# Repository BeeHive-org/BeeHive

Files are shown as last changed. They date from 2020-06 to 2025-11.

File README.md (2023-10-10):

# BeeHive - a flexible platform for connecting different sensors and actuators

## Intro

This project started as a collaboration between [Ihor Sobianin](https://github.com/isobianin/) and [Andre Chagas](https://github.com/amchagas/), after some chats about improving the [FlyPi design](https://github.com/amchagas/flypi). 

## Hardware 

The idea here is to make a very flexible hardware system that is easy to expand/customize for lab applications. The very initial implementation consists of:
- a hub PCB - which contains:
   -  2 voltage regulators that step down voltage from 12V to 5V and supply these 3 voltages to specific pins throughout the board.
   -  a central slot for an [ESP32 WROOM](https://www.espressif.com/sites/default/files/documentation/esp32-wroom-32_datasheet_en.pdf) and the breakout of all its pins into JST connectors.
   - Two Mikroe MikroBus connectors (https://www.mikroe.com/mikrobus).
   - Two Sparkfun Qwiic connectore (https://www.sparkfun.com/qwiic).
   - A 3.3V onboard voltage regulator.

-  4 switch array with an [TPIC6B595 shift register](https://www.ti.com/lit/ds/symlink/tpic6b595.pdf) and transistors.

-  8 switch array with an [TPIC6B595 shift register](https://www.ti.com/lit/ds/symlink/tpic6b595.pdf) and transistors.

-  12V5A breakout which is based on simple barrel jack connector and JST connectors

-  power supply which are based on the [LM2596 T5](https://www.ti.com/lit/ds/symlink/lm2596.pdf) a step down switching regulator
For more details see [current design](#the-current-design) section below.  

## Software

On the software side of things we are initially running micropython, as this will offer a low entry barrier for researchers (as Python is more and more the chosen language for much of the scientific stack).

- The current implementation runs stock micropython with [OSC library](https://github.com/SpotlightKid/micropython-osc) for communication, as this will allow easy integration with [Bonsai-RX](https://bonsai-rx.org/), a powerful piece of software that has integrations with other interesting open source tools for science, such as [open ephys](https://open-ephys.org/), [DeepLab Cut](http://www.mousemotorlab.org/deeplabcut) and other proprietary but useful tools, like high speed cameras, National Instruments DAQ systems. 

- The main wish software wise for this project is to make it compatible with [Labthings](https://github.com/labthings).

---

## The current design

### The main hub:

#### Schematics

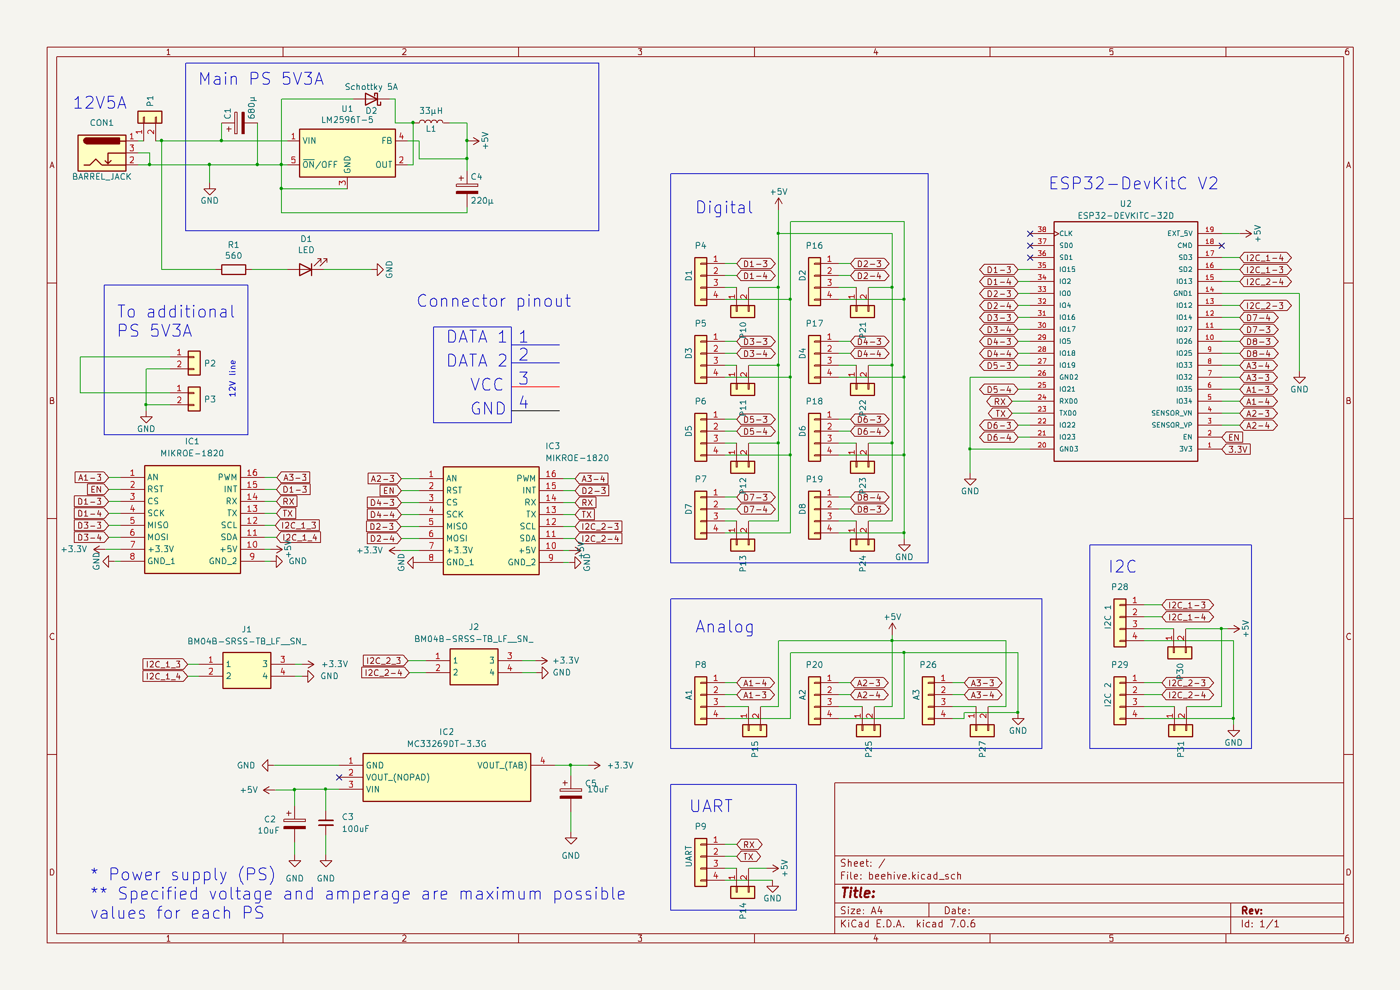
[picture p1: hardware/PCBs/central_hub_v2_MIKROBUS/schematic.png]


#### PCB

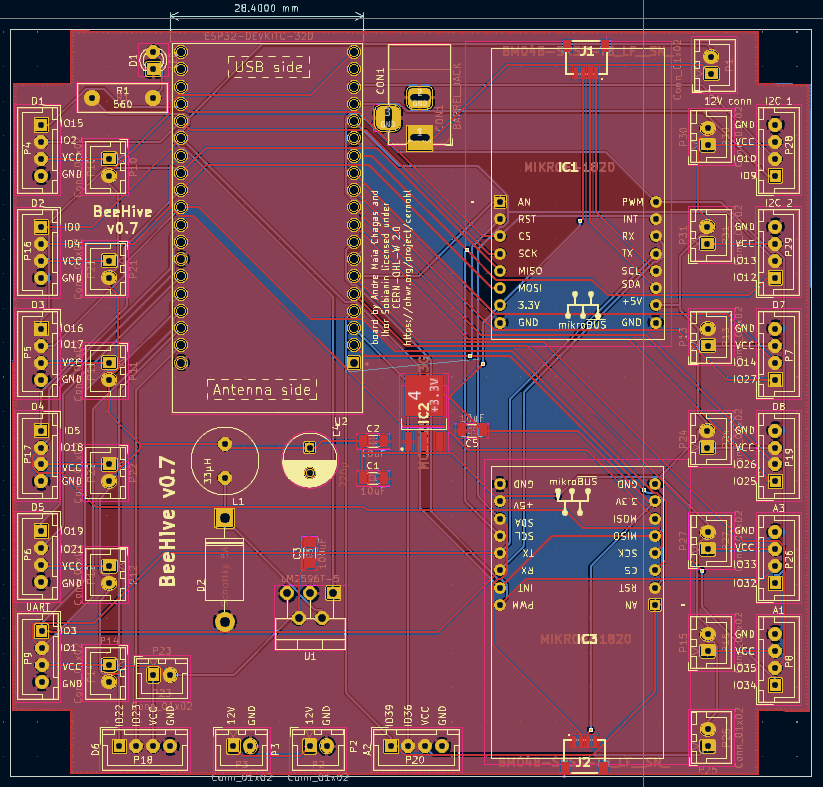
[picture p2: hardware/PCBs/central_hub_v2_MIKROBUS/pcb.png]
beehive_PCB


### The power supply module:

#### Schematics

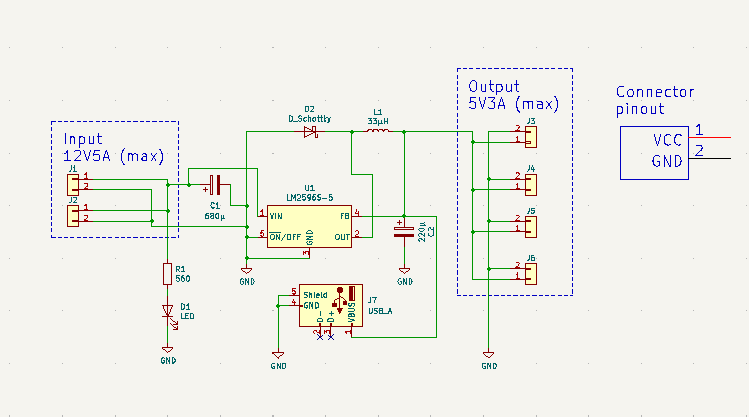
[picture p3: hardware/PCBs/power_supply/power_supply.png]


#### PCB

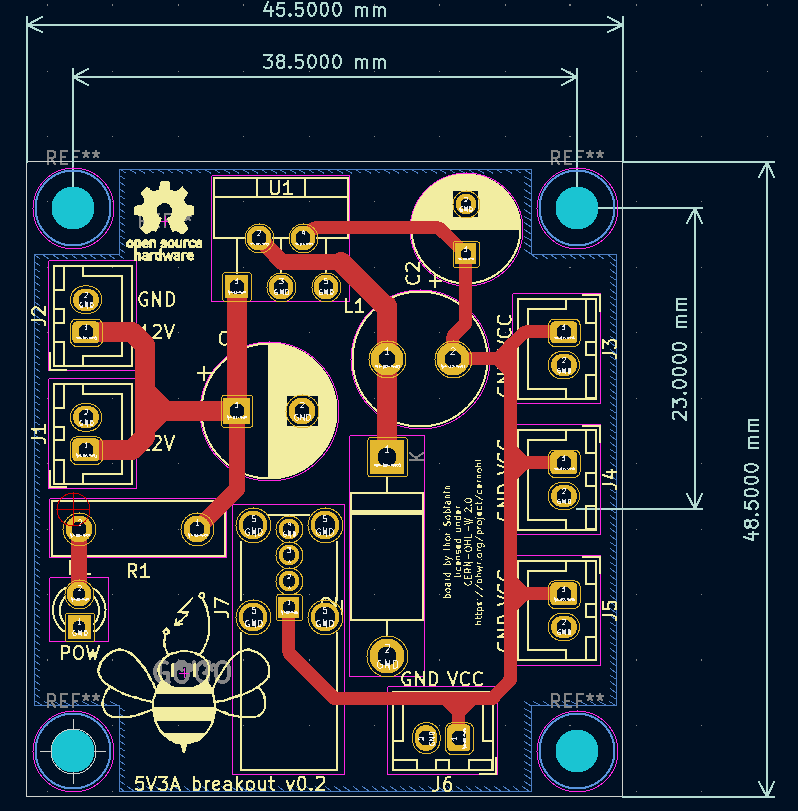
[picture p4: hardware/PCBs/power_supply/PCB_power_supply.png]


### The transistor-switch hub for 8 devices:

#### Schematics

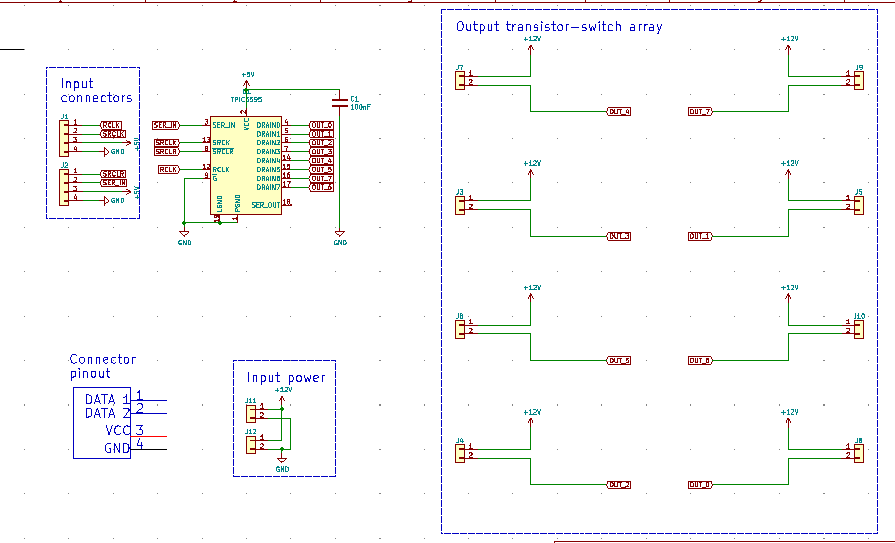
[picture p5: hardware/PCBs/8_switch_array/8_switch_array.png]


#### PCB

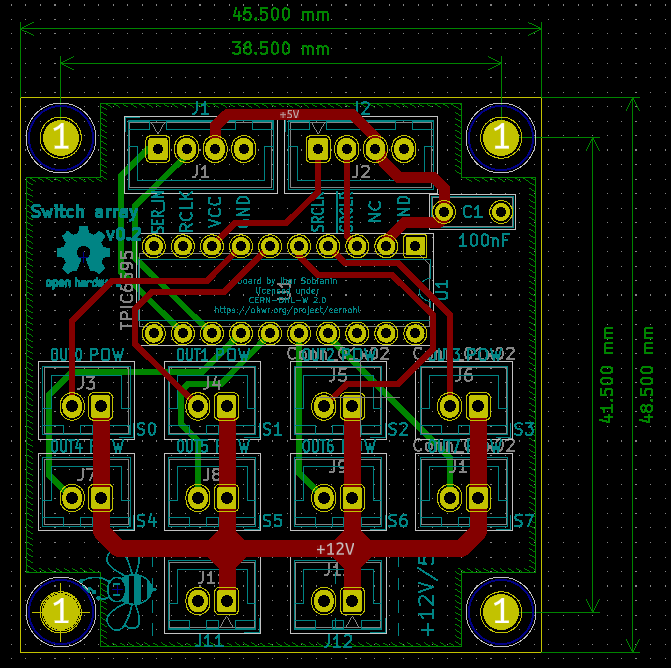
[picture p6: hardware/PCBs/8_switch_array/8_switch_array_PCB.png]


---

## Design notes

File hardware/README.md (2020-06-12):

In this folder users & collaborators will find designs and considerations about the hardware parts being developed in this project. 

### hub_PCB:
- the central part of the system, is mainly a breakout board for the ESP32 being used and two built in power supplies. 

The pin mapping of the ESP32 controller and our board can be seen here:

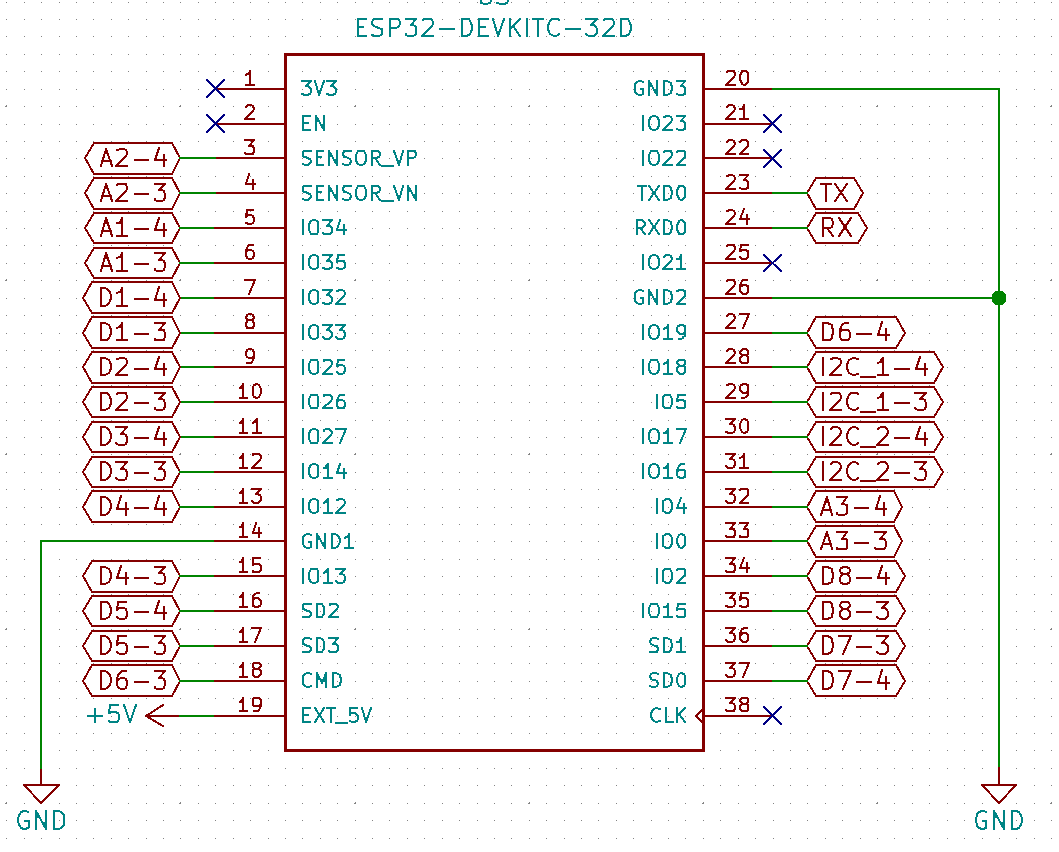
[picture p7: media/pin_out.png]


Using table 2 of this [manual](https://www.espressif.com/sites/default/files/documentation/esp32-wroom-32_datasheet_en.pdf) we can see all the options for each pin.

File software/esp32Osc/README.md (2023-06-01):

# Bonsai + BeeHive

The scripts in this folder are a first test for integration [Bonsai-RX](bonsai-rx.org) with BeeHive using [OSC](http://opensoundcontrol.org) protocol.

The idea is pretty simple for the moment:

Digital:
- make half of the Digital pins as inputs (DI)
- make half of the Digital pins as outputs (DO)
- set the ESP32 to scan the state of all DI pins and send that information out as one integer in an OSC message
- set the ESP32 to listen to OSC messages with one integer and decode that to set DO pins

Analog:
- Read all analog pin states and send that information out as an OSC message
- Set the ESP32 to listen to OSC messages (one integer to determine analog output port and another integer to determine value to be written) and write analog output value

| <Function Call> | <Return Function> | <Event> |
  
- (TODO) Send/receive servers Examples for all types of data (Bundle,float,int, bool, string,char)
- (TODO) Collect Useful functions from past projecs in upython for beeHive and some groove.
- OSC messages call functions with same name as the message
- Return values is a message called Return
- Functions are defined in uPython
- Write a automatic message Handler -> Function call -> Return value -> OSC Message
- (TODO) Timestamps
  
OSC Event Messages
    /Event

beehive: 
    /ports id
        /line 0 (pwm,analog_write,Analog_read,Digital_out,digital_in)
        /line 1 ()

/Analog_write
    /Port Value
    /PWM Value
    /Timestamp

belay: interator for step_trials, trials, sessions
    /<function name>
        /<argument Name> Value
        /<Argument Name2> Value
    /<Return>
        /<Function name> Value

Firmata:

Warp:

uOSC:

uPython:
adc.read_u16()
Pin(32, Pin.OUT)

---   

### Naming convention:
After a short discussion, naming should be given to the actual electronic function being deployed. That is, a function that turns a digital output on/off, should be called something that makes that explicit. The rationale here is that many different actions would map on to that (for instance, by turning a digital output port on, we can deliver water, turn on an led, tur on a sound, etc. so we have many to one mapping). To make it easier for users, what we can do is provide a table where all of this things are explicitly mapped:  
Timestamps?

|action|electronic equivalent|function name|example|observation|
|--|--|--|--|--|
|deliver water|turn digital output on|digital_write|digital_write(pin, value)|assuming a solenoid valve is used as control|
|turn on led|turn digital output on|digital_write|digital_write(pin, value)|assuming the LED is directly controlled by one port and not a driver|
|deliver food|send PWM signal|pwm_write|pwm_write(pin,cycle,time)|assuming mechanism to deliver food uses a motor|

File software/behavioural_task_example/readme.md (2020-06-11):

# A Behavioural task developed in BeeHive

This folder contains the code and explanations necessary to setup your first behavioural task using BeeHive!
We hope this is enough to get users going into creating their own tasks and protocols. 

### Task description:

### brief explanation on the example:
This example shows how to setup a behavioural task for conditioning mice to drink water from a spout while an LED is turned on. It counts licks, and the amount of time it took for the animal to lick the water spout once the LED has been turned on and if the animal does not reach the spout after a determined amount of time, the LED is turned off for a defined amount of time, and then turns on again. 

Here in discrete steps:
- Trial starts
- LED Turns on
  - If animals lick in pre determined time window:
    - Water pump on
    - Wait for a while so water consumes water
    - Water pump off
  - LED off - (in both cases, lick or no lick, the LED turns off)
- A predetermined amount of time is counted where nothing happens takes place (Inter trial interval)
- Start from beginning

### system specs:
- Hardware:
  - Beehive main board with ESP32 WROOM-32
  - ELP USB Camera

- Software
  - On the ESP32 we are running microPython, and the OSC library, which makes it easy for us to transfer data in a system agnostic way, but more importantly, already has an implementation in Bonsai-Rx (see point below).
  -  Bonsai-Rx is the software that runs on the computer to monitor and change the behavioural tasks. It is also used to synchronise camera data, optogenetics data, photometry data with the data coming from the ESP32.
    - At the moment, Bonsai-Rx only runs on windows computers, but there are plans for the package to be ported to GNU/Linux and other platforms. We do understand that only running on Windows is a bit limiting (also in the philosophical perspective), but we believe this is a good tradeoff, considering the wide use of this package by others (Open Ephys, DeepLab Cut etc) and the easiness it brings to add features.   

### Setting up:

- this examples leverages open source packages, and you'll need to install them before getting started:
- Bonsai-RX
- [MicroPython](<https://docs.micropython.org/en/latest/esp32/tutorial/intro.html#esp32-intro>)
- [OSC micropython library](<https://github.com/SpotlightKid/micropython-osc>)

### Other notes:
- For this example we are using MicroPython firmware stable version 1.12, taken from [here](<https://micropython.org/download/esp32/>)
- [collection of micropyhton libraries](<https://github.com/mcauser/awesome-micropython>)
- [core python libraries ported to micropython](<https://github.com/micropython/micropython-lib>)
- <https://boneskull.com/micropython-on-esp32-part-1/> has a nice walkthrough to setup things

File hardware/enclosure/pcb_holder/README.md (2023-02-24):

All freeCAD files are fully parametrised and can be used for boards outside of BeeHive family as well

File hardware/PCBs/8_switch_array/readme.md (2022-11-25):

## BeeHive system: 8 port switch array

### Hardware overview

In order to allow to use arbitrary type and number of simple tools such as low power electronics (LEDs, fans, etc) in experiments, a set of 8 switch arrays was developed. The 8 pin version utilizes a 74HC595 shift register, allowing to connect more components with less amount of pins. The power fed to the element being switched can vary from **5 to 12 volts**.

### Programming switches

An 8 switch array behaves exactly like a 74HC595 shift register but transistor switches allow bigger currents to flow through given loads

### Safety
Do not connect or disconnect connectors while power is ON. All adjustments must be done ONLY when power is OFF.

### 3D models

Current design of 8 switch version:
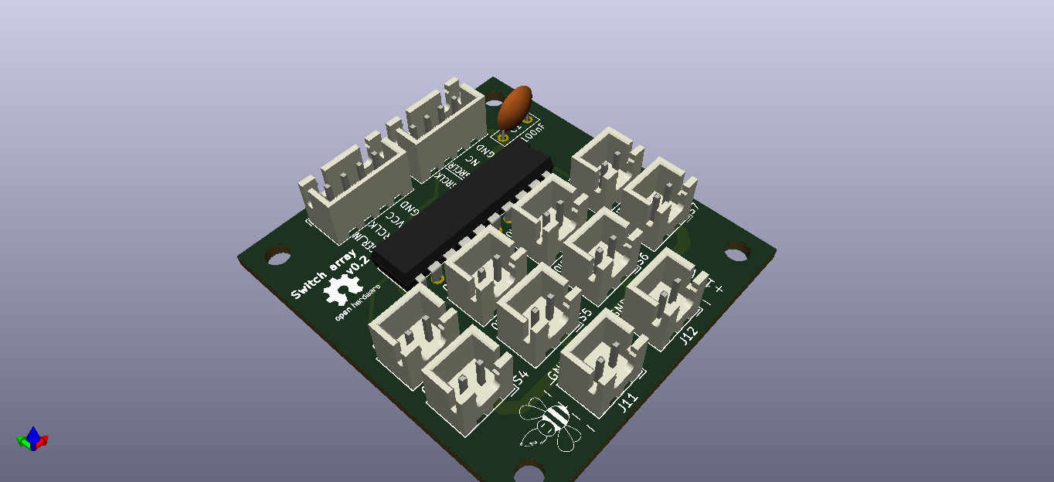
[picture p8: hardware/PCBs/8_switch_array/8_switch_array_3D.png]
8 switch version


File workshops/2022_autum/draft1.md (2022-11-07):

# First workshop plan:
Developed by Ihor & Andre 28/06/2020

The idea for this workshop is to introduce participants to physical computing and programming. To do this, we will use BeeHive and its training board.
- given that we are using micropython and can use jupyter notebooks to control the board, this will be handy as participants will leave the workshop with very good grips
on how to use these two tools (Python and Jupyter) that are widely used by biologists/Neuroscientists

Participants do not need to have previous experience with anything to attend this workshop, but need to have their own laptop.

Content:
Users need to prepare their computers for the workshop. Before it starts, they need to install anaconda, micropython kernel and download ESP32 micropython firmware
[ADD LINKS TO TUTORIALS on how  to accomplish this]

schedule:
||Monday|Tuesday|Wednesday|Thursday|Friday|
|--|--|--|--|--|--|
|09:00-10:45|Intro to Physical computing and micropython/ ESP32|Concept of timing and clocks|Introduction to  communication protocols, sending and receiving data;|||
|11:00-13:00|Exercise1: connect board and blink LED Exercise2: Read from push button (turn led on/off with button)|Exercise1: Relay push button; timing exercise||||

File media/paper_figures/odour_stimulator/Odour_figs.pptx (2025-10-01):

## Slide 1

A

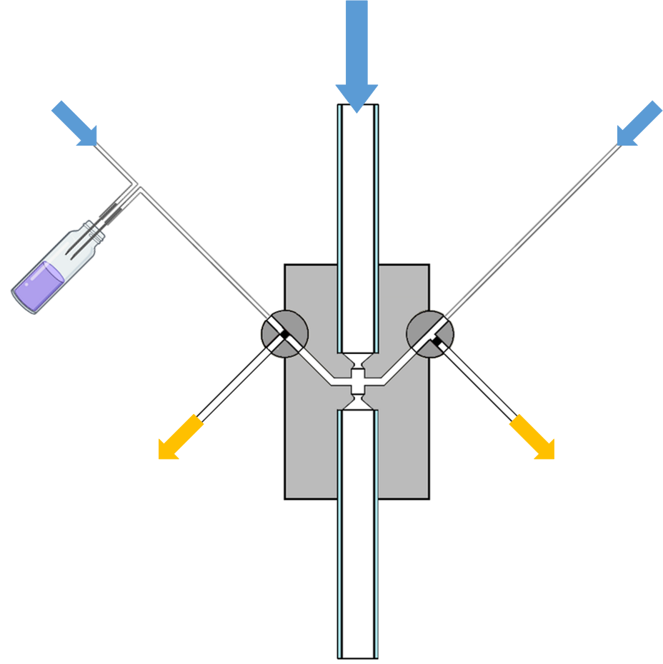
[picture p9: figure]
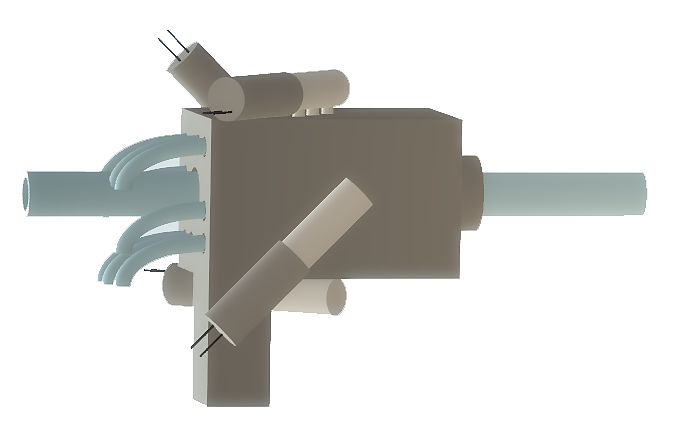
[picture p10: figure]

solenoid
valves

air
outlet

air
inlets

3D printed
mixing block

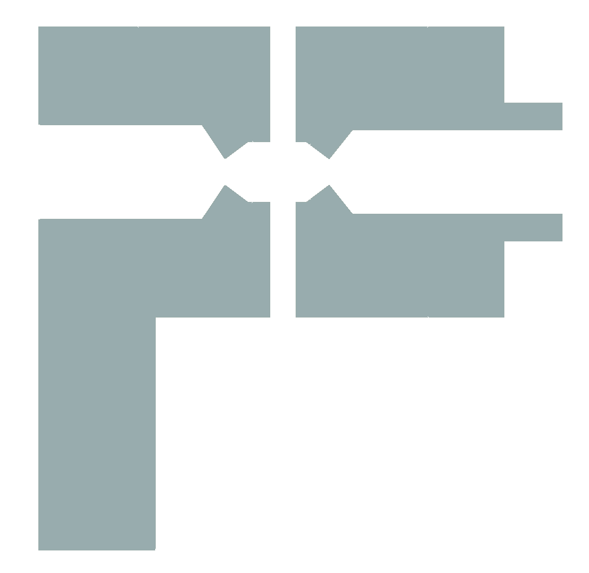
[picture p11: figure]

valved airstream

mixing
chamber

main
airstream

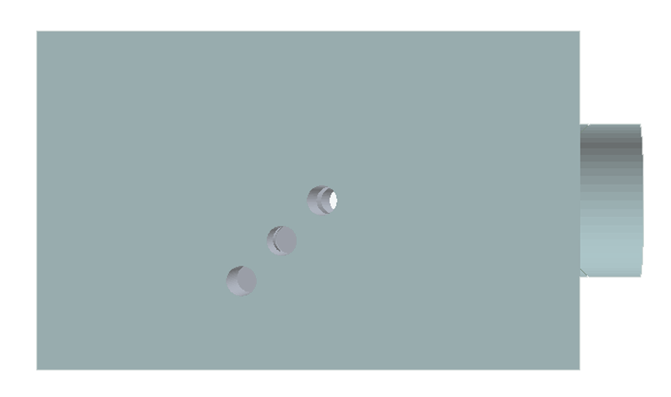
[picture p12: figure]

balance
valve

C

Olfactometer design
A) Schematic representation of single balanced odour channel consisting of two inlet airstreams (odour and balance) through the main body block into the mixing chamber, each controlled by separate three-way solenoid valves. Blue arrows indicate clean air inlets from a common regulated source. Yellow arrows indicate waste air stream outlet from each channel. B) 3D rendering of two channel stimulator. C) 2D top view rendering of two-channel stimulator with port for three-way solenoid valve. Dashed line illustrates location of (D) 2D cross section, illustrating mixing of main and valved airstreams in the mixing chamber.

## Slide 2

A

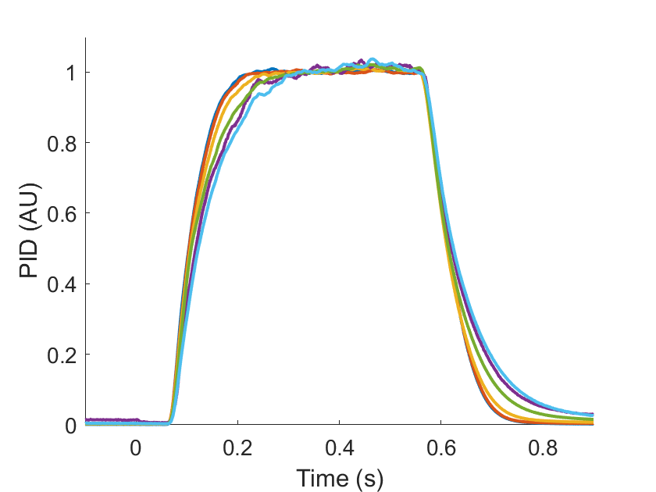
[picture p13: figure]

B

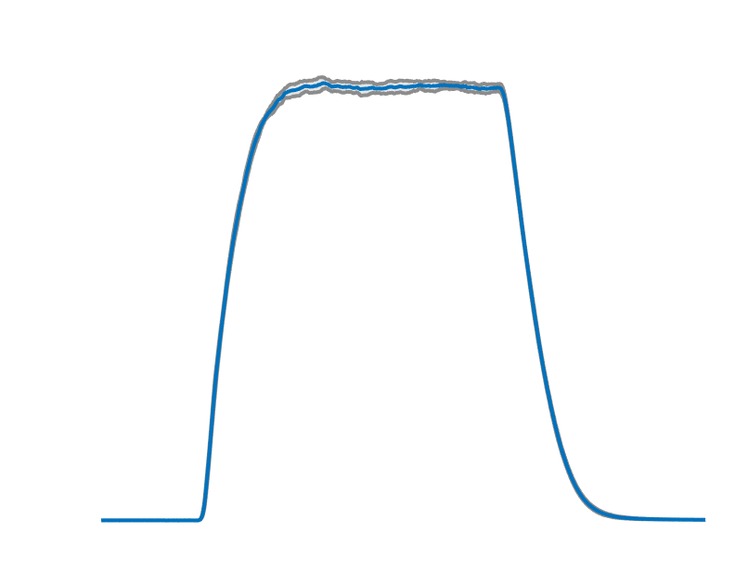
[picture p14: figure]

Methyl acetate 213 mmHg

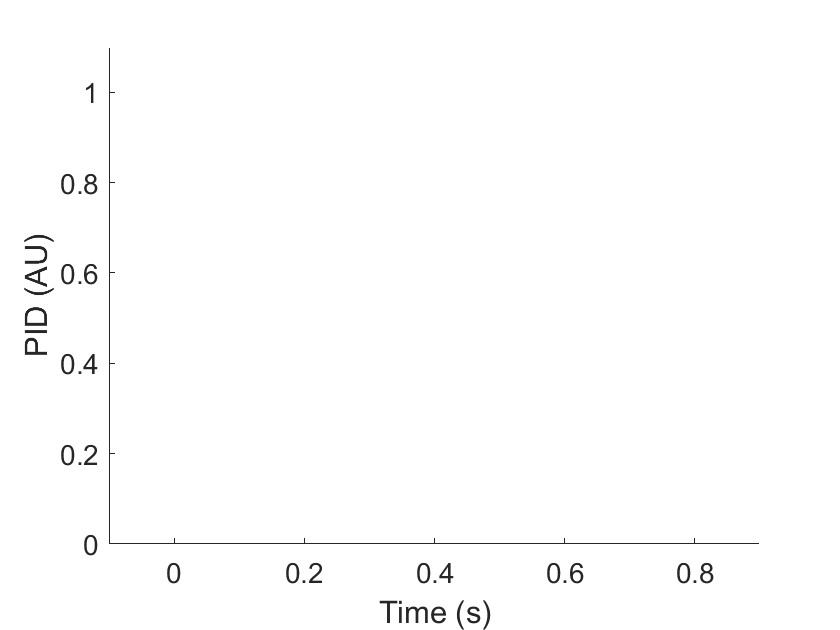
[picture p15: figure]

Methyl hexanoate 5 mmHg

Ethyl acetate 91.2 mmHg

2-heptanone 3.85 mmHg

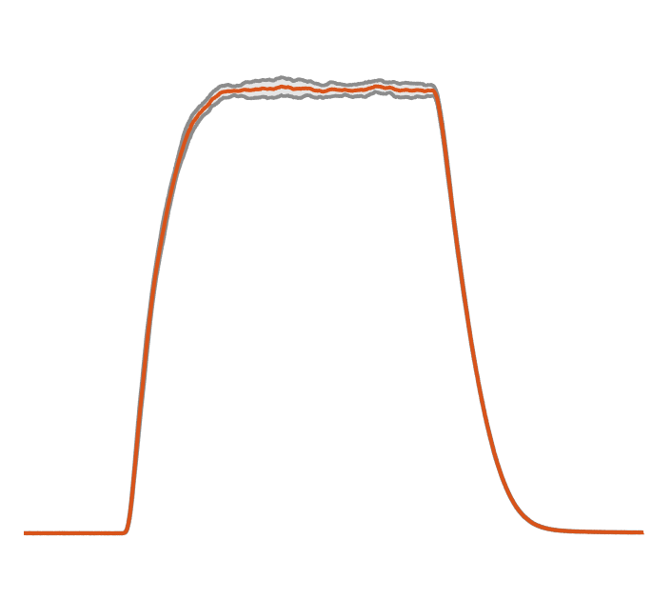
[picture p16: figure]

Ethyl butyrate 14 mmHg

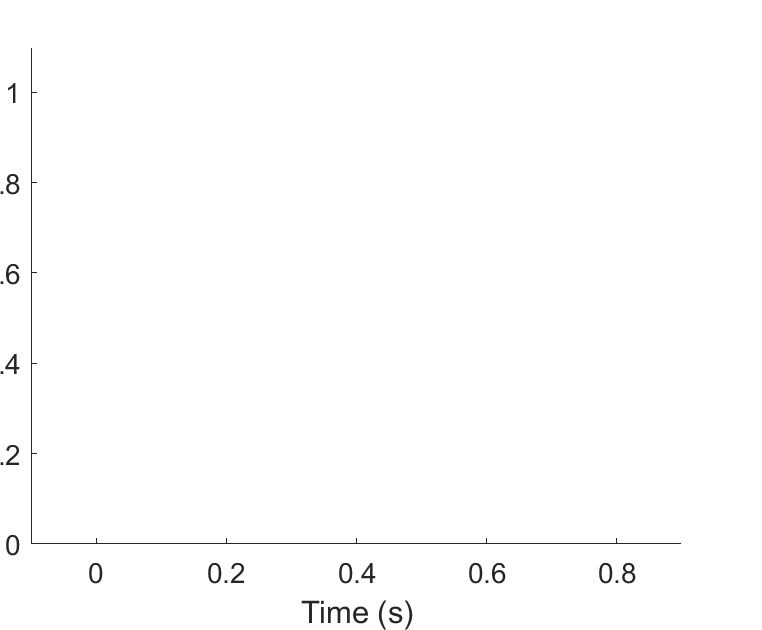
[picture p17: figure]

Benzaldehyde 0.17 mmHg

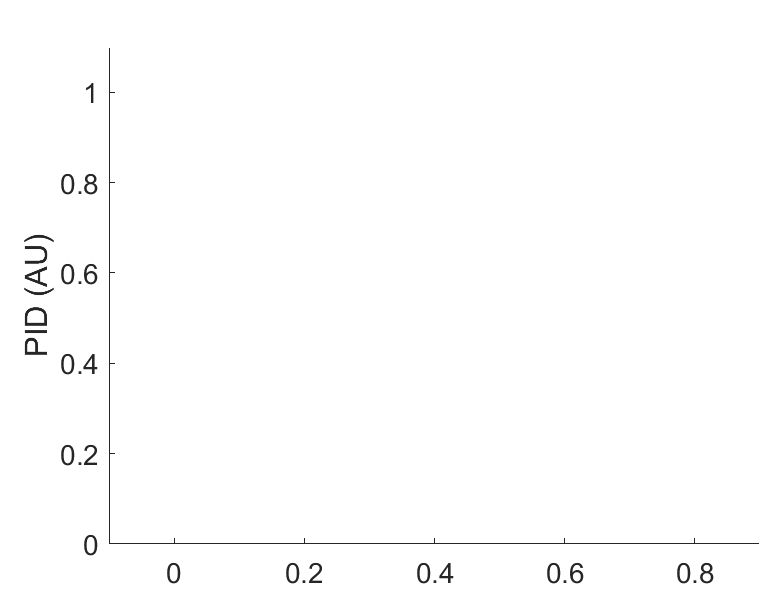
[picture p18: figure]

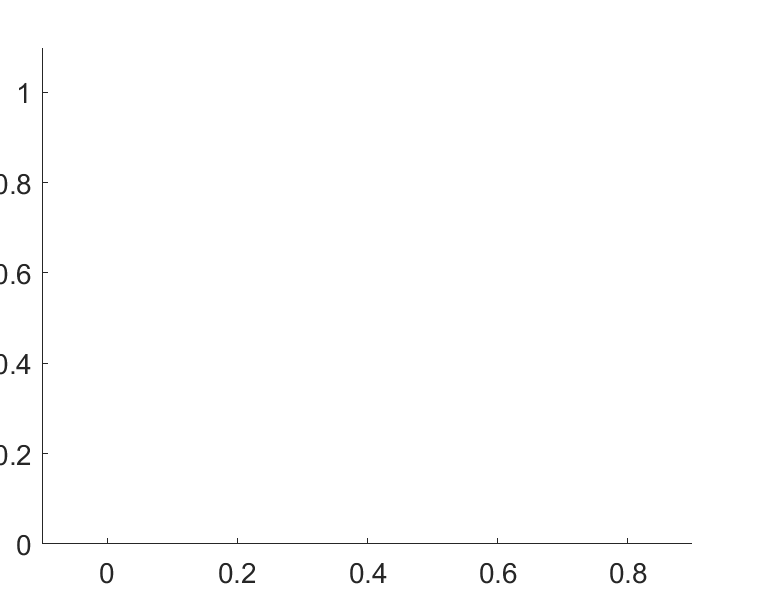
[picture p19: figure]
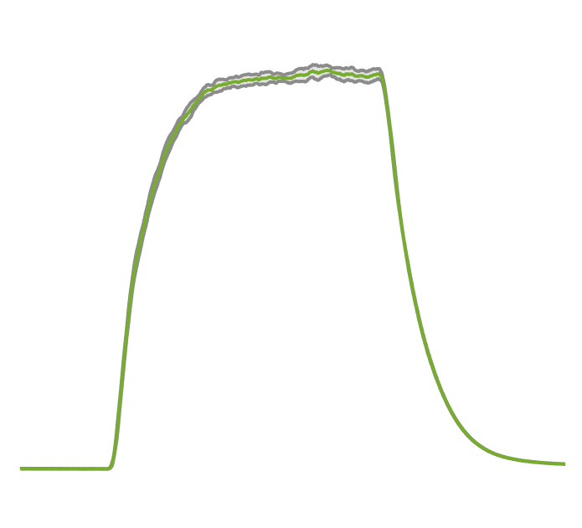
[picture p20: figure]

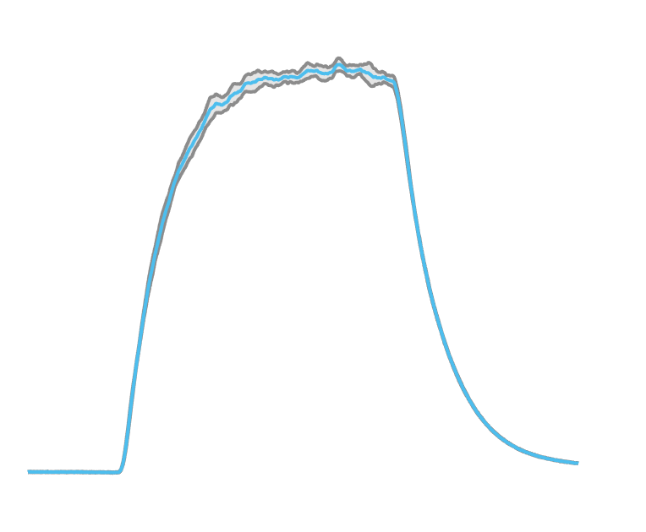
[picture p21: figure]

C

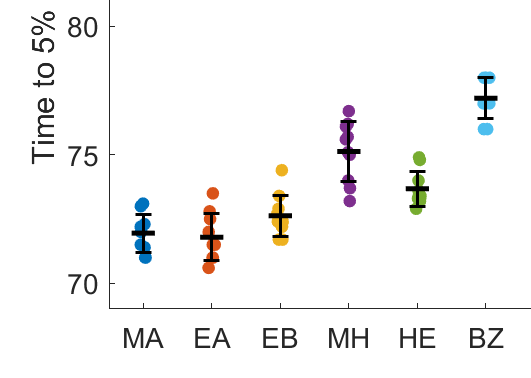
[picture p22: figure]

D

E

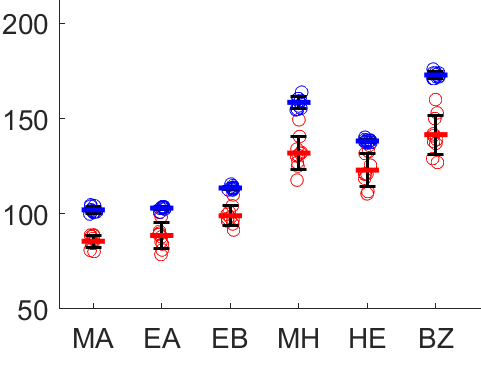
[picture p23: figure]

F

Pulse amplitude (%)

Time (ms)

Generating reproducible single odour pulse stimuli
A) 500 ms pulses of six odours with a range of volatilities. Mean signal, normalised to maximum recording for each odour. B) Each odour from (A) plotted separately and ordered by increasing vapour pressure. (C) onset precision (time from valve timing to 5 % max odour); (D) pulse variability (S.D. of PID reading from onset to onset +500ms); (E) onset (time from 10-90 % max odour) and offset (time from 90-10 % max odour); and (F) effective pulse length above a range pulse amplitudes. Odours arranged by increasing vapour pressure in panels C-F. All measurements taken with Channel 1. Shaded area of B defines mean +/- SEM; Error bars in C,E
defines mean +/- S.D.; Box plot in D defines median SD, upper/lower quartile and min/mix whiskers; n = 10 for each odour tested.

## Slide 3

A

B

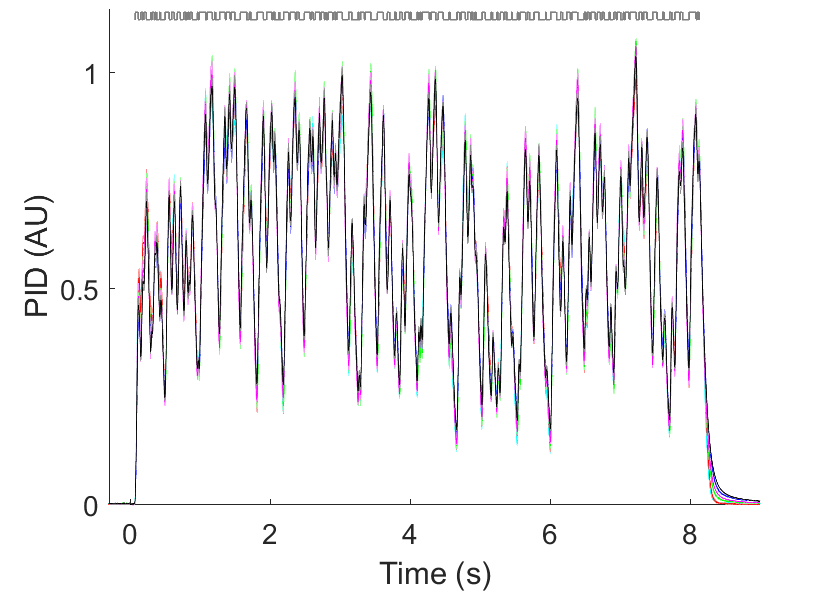
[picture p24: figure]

Time (s)

Methyl acetate
Ethyl acetate

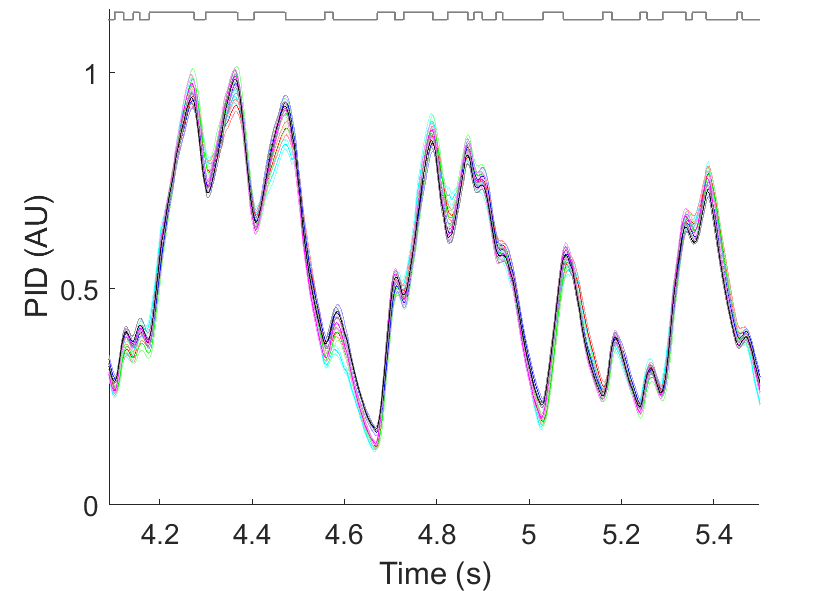
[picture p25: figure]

Time (s)

2-heptanone
Benzaldehyde

PID (AU)

Ethyl butyrate
Methyl hexanoate

Generating reproducible mixed odour stimuli
A) Normalised PID timecourse signal from all six odorants during 8.2 s randomly fluctuating odour
stimuli. (B) zoomed section. Grey lines above each panel show the olfactometer valve state.

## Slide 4

A

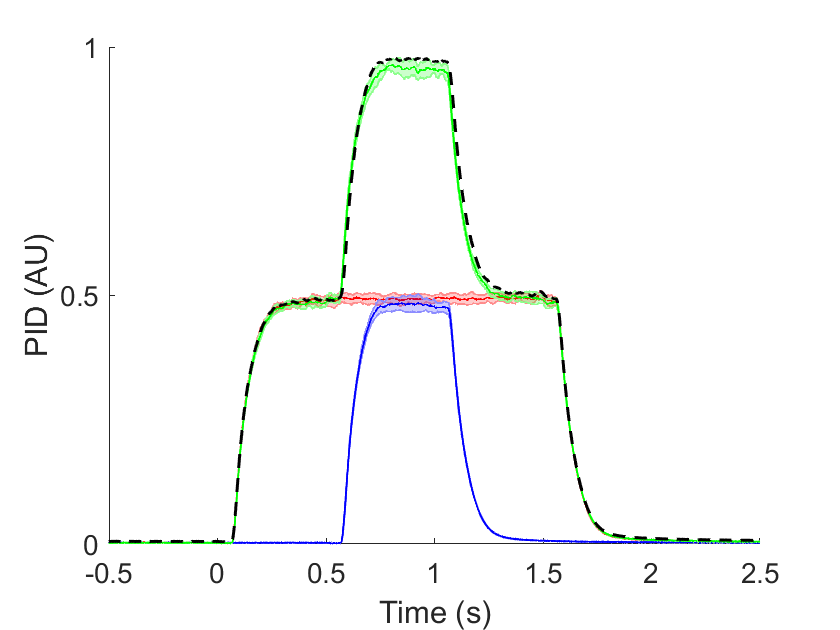
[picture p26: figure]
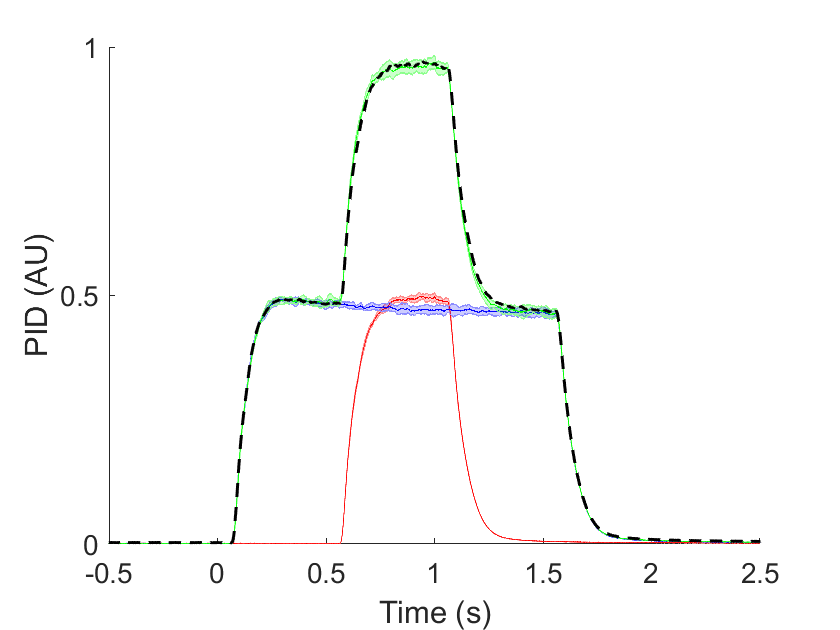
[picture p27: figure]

B

PID (AU)

C

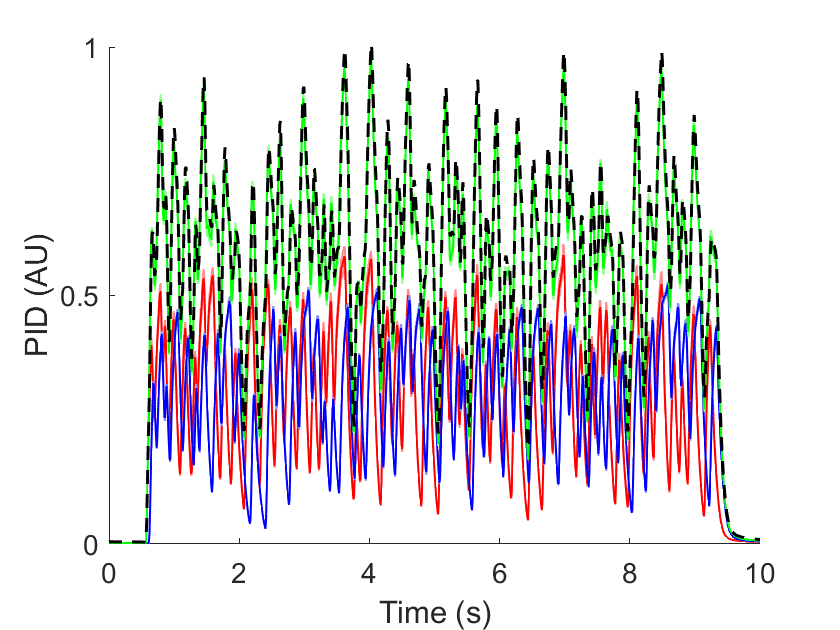
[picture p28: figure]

Time (s)

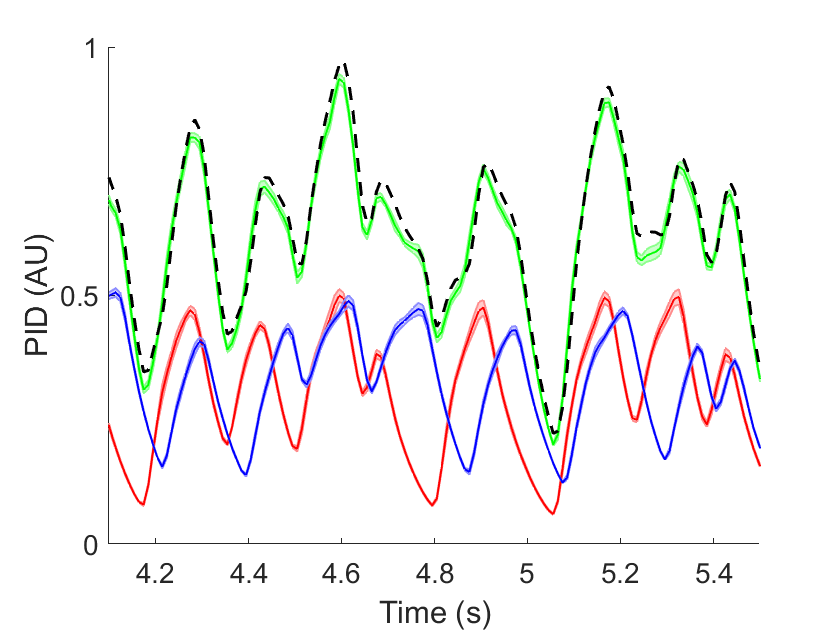
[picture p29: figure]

Time (s)

D

PID (AU)

Independence of channels
A) A short pulse delivered from channel 2 on a longer pulse from channel 1. B) A short pulse
delivered from channel 1 on a longer pulse from channel 2. Dashed line generated from adding
individual single pulses from each channel (red and blue). Comparison with actual combined
pulse (green) reveals little difference. C) The combination of the two channels can also be accurately predicted during randomly fluctuating stimuli. D) zoomed region of (C) These stimuli were generated with pure 2-heptanone in both channels.

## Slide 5

A

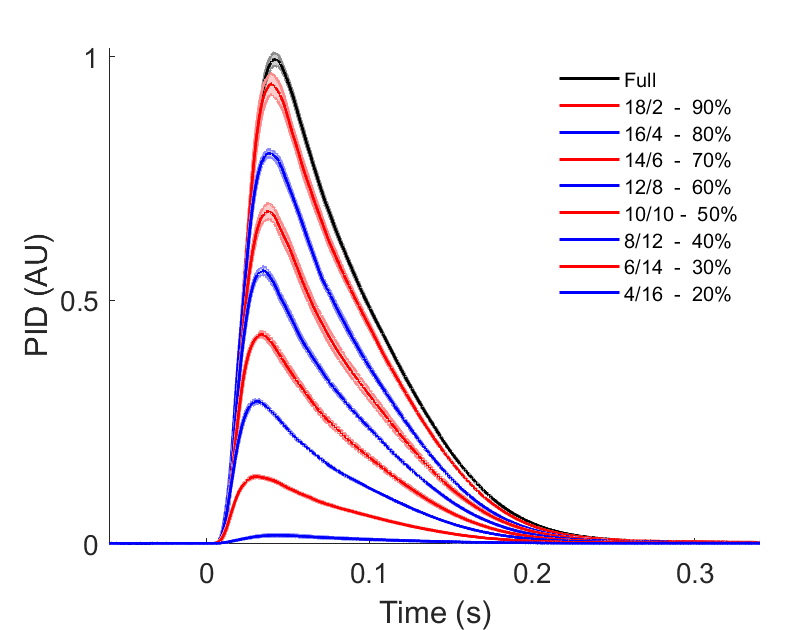
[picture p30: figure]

Time (s)

B


Time (s)

PID (AU)

PID (AU)

C


Time (s)

D

PID (AU)

5 Hz
10 Hz

Time (s)

Generating naturalistic odour stimuli
A) PID output during single cycle, generated by reducing duration of odour during 20 ms period
(e.g. 18/2 = 18 ms ON & 2 ms OFF) B) PID signal during 25 cycles, generating stable 500 ms
odour pulses of decreasing concentration. C) Prediction of a simple plume, generated by combining pulses from (A). D) Representative odour stimuli produced by opening the valve with 0.5 pulse duty. Complete pulses formed by valve cycles up to 5 Hz. These stimuli were all generated with ethyl acetate.

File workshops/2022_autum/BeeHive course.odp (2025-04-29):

## Intro to electronics and programming with Beehive

Ihor Sobianin & Andre M Chagas

November 14th-18th

## Schedule

| Monday | Tuesday | Wednesday | Thursday | Friday
Part 1 | Introduction - Physical computing - ESP32 | Timing - reaction time task - Loops | Logging data - save/read data from file | Beehive I - General concept - turn on a fan | Create your own task I
Part 2 | Introduction to training board Digital IO - Blink led - Detect button Serial communication | Analog IO - read potentiometer - set LED brightness | Time for review/issues/doubts/questions | Beehive II - Existing boards and how they can be combined for your experiments | Create your own task II

## Physical computing & research applications

Examples of projects that use electronics


## Microcontroller


## Microcontroller


## DC circuits


Ohm’s law:
I [A] = U [V] / R [Ohm]

## Ohm’s law review


## Add info about binary system and how numbers are conveyed in binary

## Binary representation-how digital computers communicate


Bits, bytes, words:


Register:

## Training board


## Connecting things for the first time

## Exercise: Digital Output

- Blink some leds on the training board!
- Steps:
  - Connect cables from the main board to appropriate section on the training board
  - Make sure to note to which IO pins on the main board the cables are connected.
- Now blink the other leds on the board, can you change the amount of time they stay on and off?

## Exercise: Digital Input

- Detect when the a button was pressed
- Steps:
  - Connect cables from the main board to appropriate section on the training board
  - Make sure to note to which IO pins on the main board the cables are connected

## Serial communication


## Conditional statements


## Loops


## Exercise: Timing

- Press a button when LED is turned ON/OFF
  - Does this seem similar to anything in Neurosciences?
  - What if we count the time in between the LED turning on and the button being pressed?

## Analog-to-digital converter


## Exercise: Analog input

- Read from a potentiometer
- How do we transform volts to integer values (ADC)

## Exercise: Analog output

- Dim an led
- How do we convert integer values to volts (DAC)

## Data Logging

- Constraints of microcontrollers
  - How much data can be transmitted at a certain amount of time
  - Time critical periods in applications
  - Record locally (SD card) or remotely (PC)
- Working together with PC
  - Capture data being transmitted/store it to file
  - Different file types.


## Exercise: Data Logging

- Show how to send data with mpremote code and than point to Dexter’s library.

## Q&A - course midpoint


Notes: Prepare some questions for the students: What is the advantage of using micropython as a programming language for microcontrollers? And disadvantages? What are microcontrollers good for? (as in how do they compare with “regular” computers? Are computers smart? What other microcontrollers could be used? Give us an application example with what you have learned so far

## Exercise at home

- Please write a small text about what kind of tool you would like to create for your research needs.
  - Try to think about how this would be implemented in code
    - This can and should be done without coding at a first stage! Create sketches, block diagrams and/or a list of logical steps on what your application needs to do.

## BeeHive I

- Please share with us the task you thought about at home
  - Lets get examples from 2-3 pairs
- Are there common points in these tasks?
  - If so, do we need to reinvent the wheel every time?
- What if we had a system with pre-configured building blocks?

## BeeHive I

Beehive presentation

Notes: Presentation about BeeHive (longer or shorter version depending on the time we have) Present beehive boards we have so far Present combinations for actual working systems Talk about the plugs and GROVE

## Exercise: BeeHive I application

- Turn on a DC motor/peltier element/fan

## BeeHive I other examples

Other boards and actuators/sensors that can be controlled with them.

## BeeHive II

- Using the existing blocks for your experiments
  - Match your task with existing beehive boards

## Create your own system

- Using the training board and your new coding skill, start implementing the programming logic for your task!

## Closing remarks

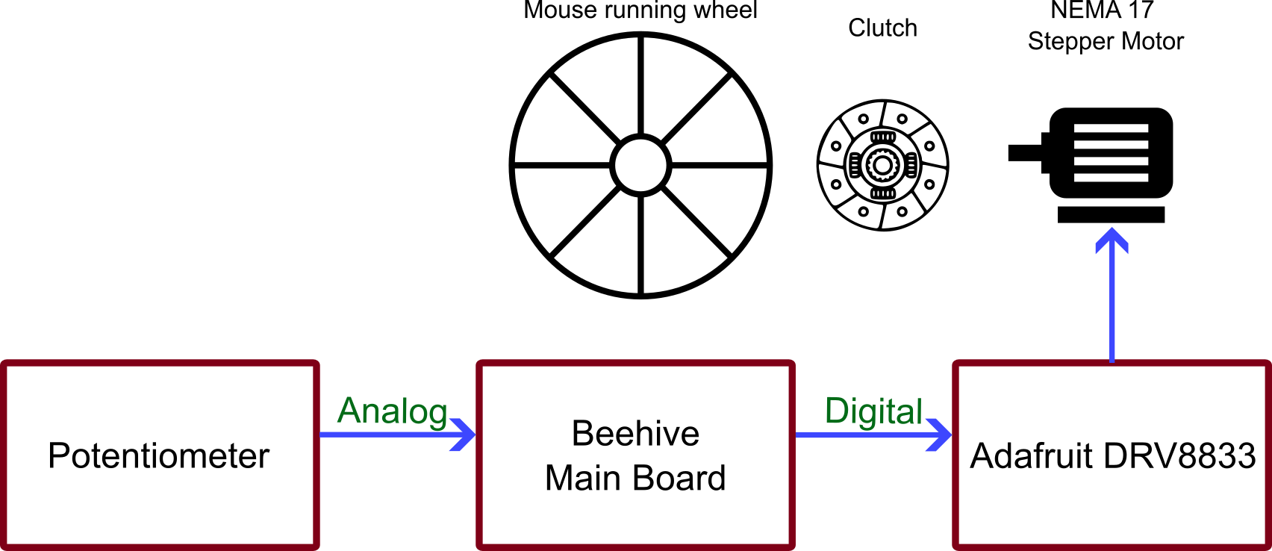
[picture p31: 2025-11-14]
media/paper_figures/mouse_wheel/mouse_wheel.png

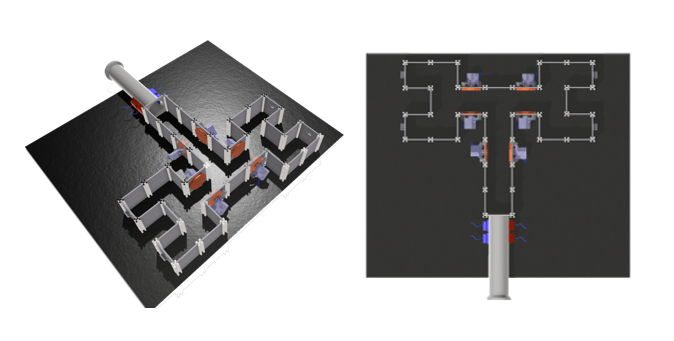
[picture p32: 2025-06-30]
media/paper_figures/maze/model.png

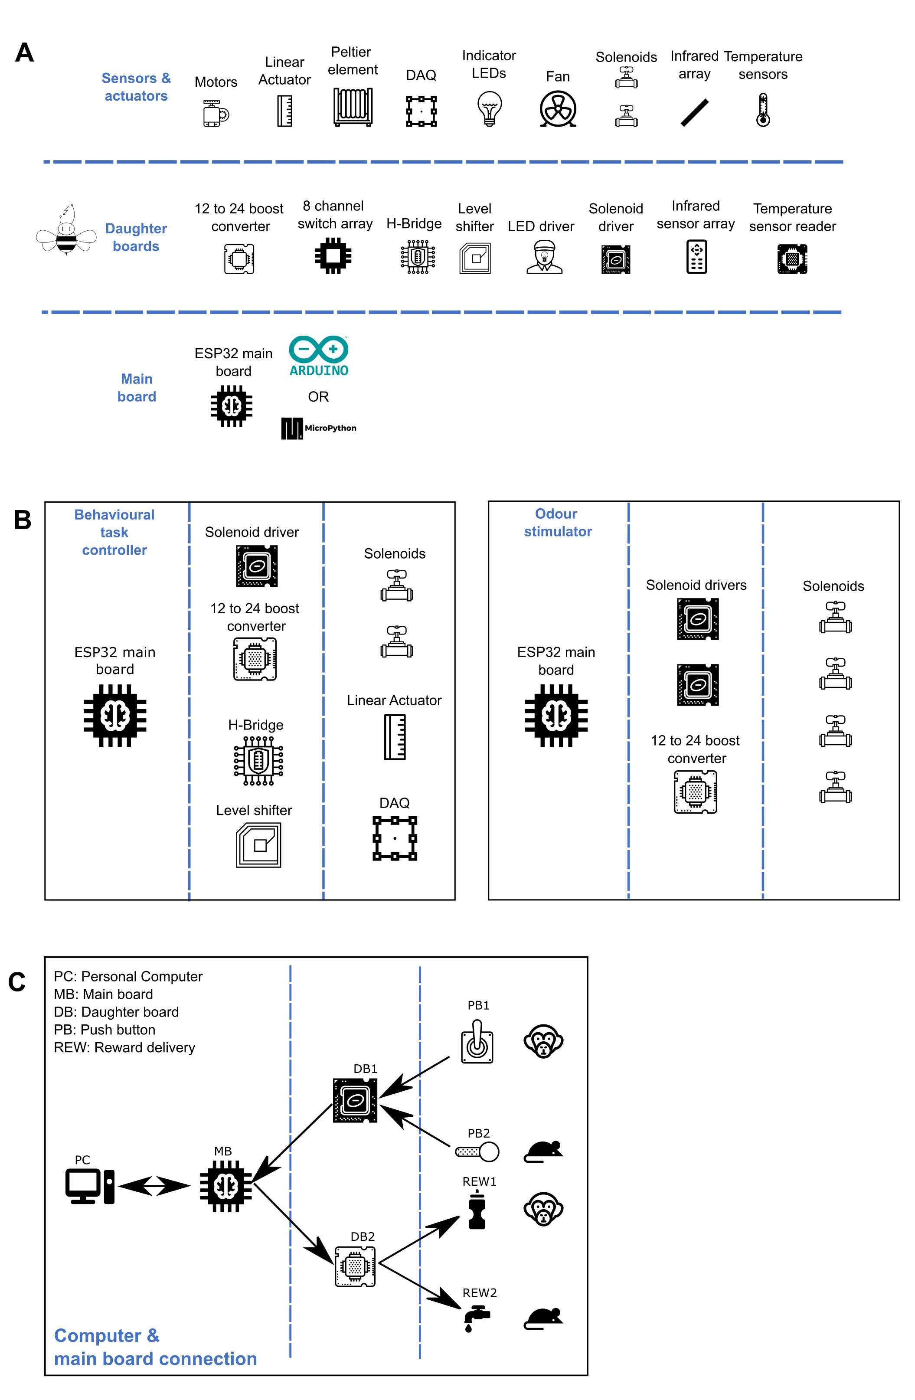
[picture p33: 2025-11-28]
media/paper_figures/system_overview_schematic/fig1_1.png

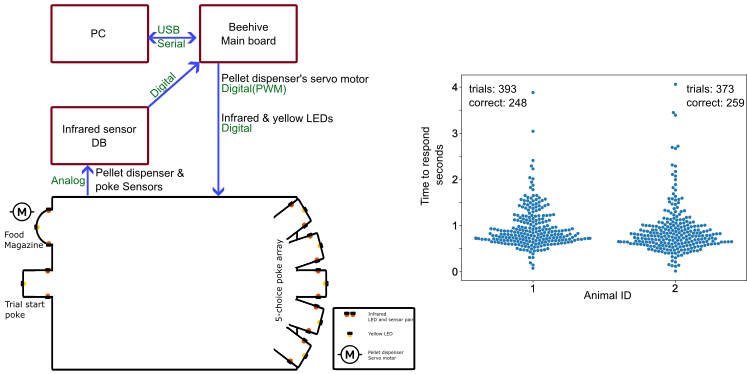
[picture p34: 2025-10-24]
media/paper_figures/5-csrtt/complete_figure.png

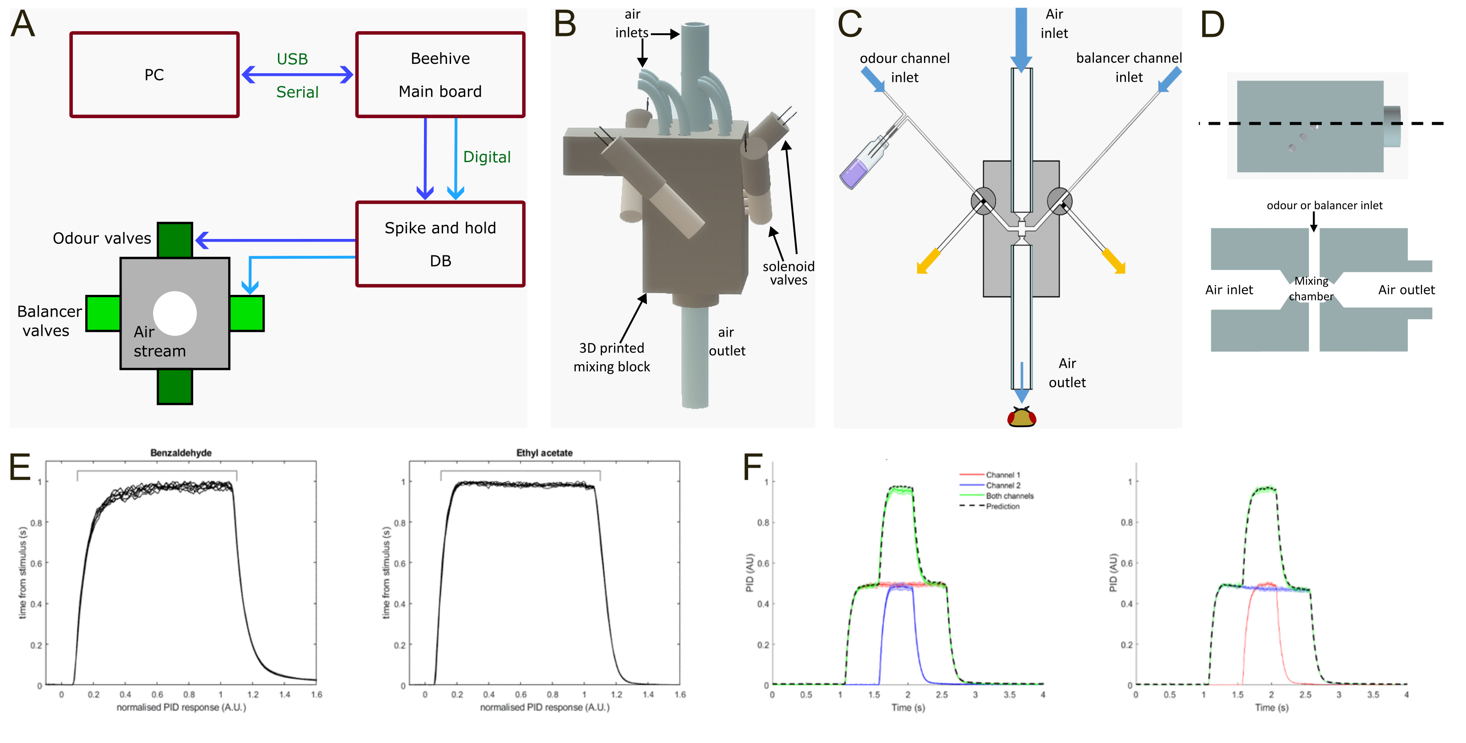
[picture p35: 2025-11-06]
media/paper_figures/odour_stimulator/v3.png

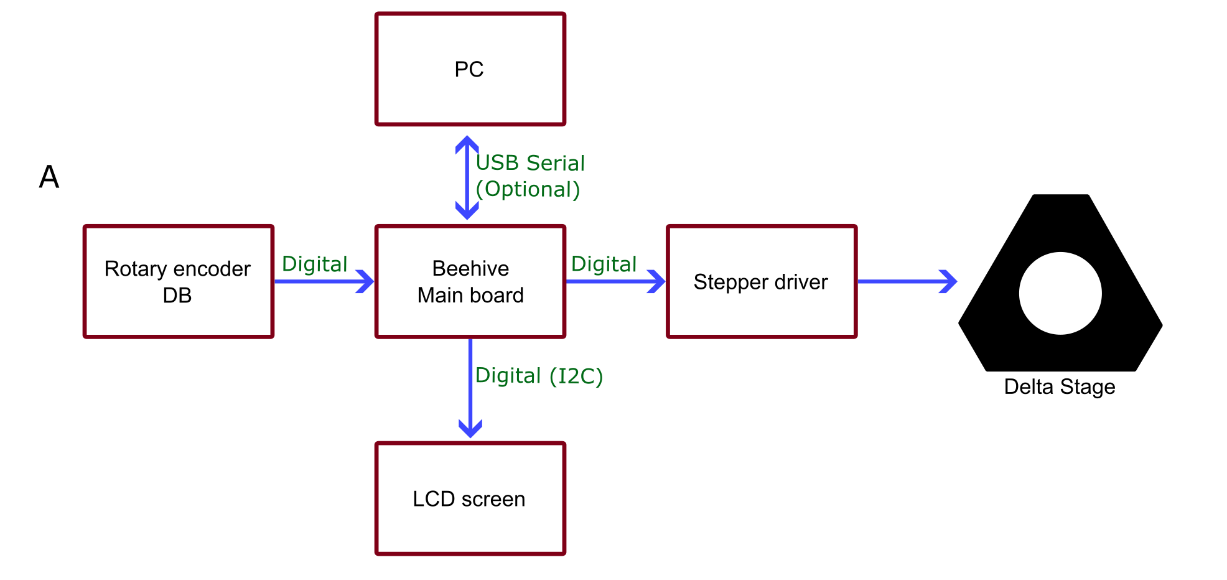
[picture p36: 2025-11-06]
media/paper_figures/stage_controller/rect4.png

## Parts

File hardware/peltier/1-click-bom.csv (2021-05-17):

References | Qty | Description | Manufacturer | MPN | Manufacturer | MPN | Manufacturer | MPN | Manufacturer | MPN | Manufacturer | MPN | Manufacturer | MPN | Manufacturer | MPN | Manufacturer | MPN | Manufacturer | MPN | Digikey | Mouser | RS | Newark | Farnell
U1;U2 | 2 | TC4420 footprint PDIP-8 | Microchip | TC4420CPA | Microchip | TC4420EPA |  |  |  |  |  |  |  |  |  |  |  |  |  |  | TC4420EPA-ND | 579TC4420EPA | 6811124 |  | 9762566
Q1;Q2 | 4 | IRF9Z34NPBF or IRF4905PbF footprint TO-220AB | Infineon | IRF4905PBF | Infineon | IRF9Z34NPBF |  |  |  |  |  |  |  |  |  |  |  |  |  |  | IRF9Z34NPBF-ND | 942IRF9Z34NPBF | 5409799 |  | 8648689
Q3;Q4 | 4 | IRFZ24NPBF or IRFZ44NPbF footprint TO-220AB | Infineon | IRFZ44NPbF | Infineon | IRFZ44NPBF |  |  |  |  |  |  |  |  |  |  |  |  |  |  | IRFZ44NPBF-ND | 942IRFZ44NPBF | 5409777 |  | 1544411
R3;R4;R5;R6 | 4 | Resistor 47 ohm 250mW through-hole | TE Connectivity | LR1F47R | TE Connectivity | ROX1SJ47R |  |  |  |  |  |  |  |  |  |  |  |  |  |  | A131472CT-ND | 279LR1F47R | 148174 |  | 1738569
R1;R2;R7;R8 | 4 | Resistor 1k ohm 250mW through-hole | TE Connectivity | CFR16J1K0 | TE Connectivity | ROX2SJ1K0 |  |  |  |  |  |  |  |  |  |  |  |  |  |  | A104669CT-ND | 279ROX2SJ1K0 | 2141951 |  | 1738638
R6; | 1 | Resistor 4.7k ohm 250mW through-hole | TE Connectivity | CFR25J4K7 | TE Connectivity | LR1F4K7 |  |  |  |  |  |  |  |  |  |  |  |  |  |  | A105962CT-ND | 279CFR25J4K7 | 1251136 |  | 2329685
R9; | 1 | Resistor 220 ohm 250mW through-hole | Yageo | MFR-25FBF52-220R | TE Connectivity | LR1F220R |  |  |  |  |  |  |  |  |  |  |  |  |  |  | MFR-25FBF52-220R-ND | 279LR1F220R | 148348 |  | 2330065
R10; | 1 | Resistor 560 ohm 250mW through-hole | TE Connectivity | CFR25J560R | KOA Speer | CF1/2CT52R561J |  |  |  |  |  |  |  |  |  |  |  |  |  |  | 2019-CF1/2CT52R561JCT-ND | 279CFR25J560R | 131227 |  | 2329690
C2;C3;C6;C7 | 4 | 100nF Capacitor Disc | Multicomp | MCFYU6104Z6 | KEMET | C052C104K5R5CA | KEMET | C052K104K5X5CA | KEMET | C052T104K5X5CS | KEMET | C321C104K5R5HA | KEMET | CK05BX104K | Vishay | K104K15X7RF5TH5 | Vishay | K104Z15Y5VF5TL2 | Multicomp | MC0805B104K500A5.08MM | BC1101CT-ND | 594K104K15X7RF5TH5 | 8523277 | 73M2154 | 2395773
C1;C4;C5 | 3 | 22uF CP_Radial_D5.0mm_P2.00mm | Panasonic | ECA-1HM220 |  |  |  |  |  |  |  |  |  |  |  |  |  |  |  |  | P5179-ND | 667ECA1HM220 | 2286880 |  | 9693777
L1; L2; | 2 | INDUCTOR 33�H Neosid MA-Bs75 | Bourns | RLB0914-330KL | Bourns | RLB9012-330KL |  |  |  |  |  |  |  |  |  |  |  |  |  |  | RLB9012-330KL-ND | 652RLB9012330KL | 8118853 | 61J7916 | 2309242
J1;J5 | 2 | CONN HEADER XH TOP 2POS 2.5MM | JST | B2B-XH-A (LF)(SN) | JST | B2B-XH-A(LF)(SN) |  |  |  |  |  |  |  |  |  |  |  |  |  |  | 455-2247-ND |  | 8201554 | 73M9415 | 1516276
J2;J3 | 2 | CONN HEADER XH TOP 4POS 2.5MM | JST | B4B-XH-A (LF)(SN) | JST | B4B-XH-A(LF)(SN) |  |  |  |  |  |  |  |  |  |  |  |  |  |  | 455-2249-ND |  | 8201551 |  | 1516278
D1;D2 | 2 | 3mm LED any colour | Bivar Inc | ELM 5-065 | Bivar | ELM 5-065 |  |  |  |  |  |  |  |  |  |  |  |  |  |  | 492-2284-ND | 749ELM5065
cables | 16 | JUMPER SXH-001T-P0.6 X2 10"" | JST | ASXHSXH22K254 |  |  |  |  |  |  |  |  | 455-4223-ND
connectors 2pin | 4 | CONN HOUSING 2.5MM 2POS | JST | XHP-2 |  |  |  |  |  |  |  |  | 455-2266-ND |  | 8201611 |  | 1516264
connectors 4pin | 6 | CONN HOUSING 2.5MM 4POS | JST | XHP-4 |  |  |  |  |  |  |  |  | 455-2267-ND |  | 8201618 |  | 1516266

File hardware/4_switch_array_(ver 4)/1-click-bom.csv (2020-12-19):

References | Qty | Description | Manufacturer | MPN | Manufacturer_1 | MPN_2 | Manufacturer_3 | MPN_4 | Manufacturer_5 | MPN_6 | Manufacturer_7 | MPN_8 | Digikey | Mouser | RS | Newark | Farnell
Q1; Q2; Q3; Q4; | 4 | 1A NPN | ON Semiconductor/fairchild | PN2222ATF |  |  |  |  |  |  |  |  | PN2222ATFCT-ND | 512-PN2222ATF | 806-1296 | 31Y3451 | 2453811
R1; R2; R3; R4; | 4 | Resistor 270 ohm 250mW through-hole | Stackpole Electronics | CF14JT270R | Yageo | MFR-25FBF52-220R | TE Connectivity | CFR16J270R | Ohmite | OD271JE | Kamaya | RC1/4271JB | CF14JT270RCT-ND | 791-RC1/4-271JB | 148360 | 95W5736 | 2329504
J1;J2; | 2 | CONN HEADER XH TOP 4POS 2.5MM | JST | B4B-XH-A (LF)(SN) |  |  |  |  |  |  |  |  | 455-2249-ND |  | 820-1551 |  | 1516278
J3; J4; J5; J6; J7; | 5 | CONN HEADER XH TOP 2POS 2.5MM | JST | B2B-XH-A (LF)(SN) |  |  |  |  |  |  |  |  | 455-2247-ND |  | 8201554P | 73M9415 | 1516276

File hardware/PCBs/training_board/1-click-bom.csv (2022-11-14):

References | Qty | Description | Manufacturer | MPN | Manufacturer | MPN | Digikey | Mouser | RS | Newark | Farnell | LCSC | JLC Assembly
d1;d2;d3;d4;d5;d6;d7;d8;d9;d10;d11;d12;d13;d14;d15;d16;d17;d18;d21;d22 | 20 | indicator leds | Marktech Optoelectronics | MT7403A-UR-A |  |  | 1125-1181-ND | 193MT7403AURA
d19;d20 | 2 | flyback diodes | Vishay | 1N5822-E3/73 | Diodes Inc. | SB5100-T | 1N5822-E3/73GICT-ND | 6251N5822E3/73 | 7514843 |  | 1336553
j1;j2;j3;j4;j5;j6;j7;j8;j9;j16 | 10 | connector | JST | B4B-XH-A (LF)(SN) |  |  | 455-2249-ND |  |  |  | 1516278
u3 | 1 | tpic6595n | Texas Instruments | TPIC6B595N | Texas Instruments | TPIC6C595N | 296-1956-5-ND | 595TPIC6B595N | 528145 |  | 3120896
RV1;RV2 | 2 | potentiometer | ALPS | RK09K1130AH1 | Bourns | PTV09A-4025F-B503 | PTV09A-4025F-B503-ND | 688RK09K1130AH1 | 7293587 |  | 1191725
U1;U2 | 2 | temp sensor | Maxim Integrated | DS18B20+ |  |  | DS18B20+T&RCT-ND
sw1;sw2;sw3;sw4 | 4 | push buttons | TE Connectivity | 1825910-2 |  |  | 450-1649-ND | 506FSM2JH | 4791390 |  | 2469975
RLY1;RLY2 | 2 | relays | omron | G5LE-1-36 DC5 |  |  | G5LE-1-36DC5-ND | 653G5LE136DC5 |  |  | 1798616
r1;r;2;r3;r4;r5;r6;r7;r13;14;r15;r16;r20;r21;r22;r23;r24;r25 | 20 | resistor 220 ohm | Yageo | CFR-25JB-52-220R |  |  | 220QBK-ND | 603CFR25JB52220R |  |  | 3952580
r18 | 1 | resistor 4.7kohm | Stackpole Electronics | CF14JT4K70 |  |  | CF14JT4K70CT-ND
r8;r9;r10;r12; | 1 | resistor 1kohm | Stackpole Electronics | CF14JT1K00 |  |  | CF14JT1K00CT-ND
r19;r26 | 1 | resistor 330ohm |  | CF14JT330R |  |  | CF14JT330RCT-ND

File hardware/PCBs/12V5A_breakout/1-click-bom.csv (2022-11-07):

References | Qty | Description | Manufacturer | MPN | Manufacturer_1 | MPN_2 | Manufacturer_3 | MPN_4 | Manufacturer_5 | MPN_6 | Manufacturer_7 | MPN_8 | Digikey | Mouser | RS | Newark | Farnell
J1; | 1 | 2.1mm socket | Cliff | FC68148 DC10A | Lumberg | NEB 21 R | Cliff | FC68148 | Gravitech | CON-SOCJ-2155 | Parallax | 452-00007 | 452-00007-ND | 992CONSOCJ2155 | 5051609 | 08WX2563 | 224959
J2; J3; J4; J5; J6; J7; J8; J9; J10; | 9 | CONN HEADER XH TOP 2POS 2.5MM | JST | B2B-XH-A (LF)(SN) |  |  |  |  |  |  |  |  | 455-2247-ND |  | 8201554P | 73M9415 | 1516276
R1; | 1 | Resistor 560 ohm 250mW through-hole | Stackpole Electronics | CF14JT270R | Yageo | MFR-25FBF52-220R | TE Connectivity | CFR16J270R | Ohmite | OD271JE | Kamaya | RC1/4271JB | CF14JT270RCT-ND | 791-RC1/4-271JB | 148360 | 95W5736 | 2329504
D1 | D2; | 2 | 3mm LED any colour | Bivar Inc | ELM 5-065 | 492-2284-ND

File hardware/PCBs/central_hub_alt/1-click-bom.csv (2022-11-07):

References | Qty | Description | Manufacturer | MPN | Manufacturer | MPN | Manufacturer | MPN | Manufacturer | MPN | Manufacturer | MPN | Digikey | Mouser | RS | Newark | Farnell
U1; | 1 | LM2596 5v | ITO-220 | Texas Instruments | Texas Instruments | LM2596T-5.0/NOPB |  |  |  |  |  |  | LM2596T-5.0/NOPB-ND | 926LM2596T5.0/NOPB | 5333743 |  | 3008166
U3; | 1 | ESP32-DevKitC-VIB |  |  |  |  |  |  |  |  |  |  | 1965-ESP32-DEVKITC-VIE-ND
P1;P2;P3;P4;P5;P6;P7;P8;P9;P10;P11;P12;P13;P14; | 14 | CONN HEADER XH TOP 4POS 2.5MM | JST | B4B-XH-A (LF)(SN) |  |  |  |  |  |  |  |  | 455-2249-ND |  | 8201551 |  | 1516278
P15;P16 | 2 | CONN HEADER XH TOP 2POS 2.5MM | JST | B2B-XH-A (LF)(SN) |  |  |  |  |  |  |  |  | 455-2247-ND |  | 820-1554 |  | 1516276
L1; | 1 | INDUCTOR 33µH Neosid MA-Bs75 | Bourns | RLB0914-330KL | Bourns | RLB9012-330KL |  |  |  |  |  |  | RLB9012-330KL-ND | 652RLB0914330KL | 8118853 |  | 2309242
D1; | 1 | Diode Schottky 5A DO-201AD | Vishay | 1N5822-E3/73 | Zetex | SB5100-T |  |  |  |  |  |  | 1N5822-E3/73GICT-ND | 6251N5822E3/73 | 7514843 |  | 1336553
CON1; | 1 | 2.1mm socket | Cliff | FC68148 DC10A | Lumberg | NEB 21 R | Cliff | FC68148 | Gravitech | CON-SOCJ-2155 | Parallax | 452-00007 | SC1313-ND | 992CONSOCJ2155 | 5051609 |  | 1217037
C1; | 1 | 680µF Capacitor | Rubycon | 16ZL680MEFC10X16 | Panasonic | EEU-FC1A681 | Panasonic | EEU-FP1E681 |  |  |  |  | 1189-3978-ND | 667EEUFP1E681 | 1793151 |  | 2911616
C2; | 1 | CAP ALUM 220UF 20% 25V RADIAL | Panasonic | EEU-FM1E221 | Panasonic | ECA-1CM221B | Panasonic | ECE-A0GKS221 | Panasonic | EEU-EB1A221S |  |  | P13456-ND | 667ECA1CM221B | 7472036 |  | 9451099

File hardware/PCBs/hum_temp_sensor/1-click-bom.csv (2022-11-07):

References | Qty | Description | Manufacturer | MPN | Manufacturer_1 | MPN_2 | Manufacturer_3 | MPN_4 | Manufacturer_5 | MPN_6 | Manufacturer_7 | MPN_8 | Digikey | Mouser | RS | Newark | Farnell
A1; | 1 | DHT11 or DHT22 | - | - | - |  |  |  |  |  |  |  | 1528-1228-ND
RV1; | 1 | 3362P-1-103 10k Ohm | Bourns | 3362P-1-103 | ON Semiconductor |  |  |  |  |  |  |  | 3362P-1-103LF
R1; | 1 | Resistor 5.1k ohm 250mW through-hole | Stackpole Electronics | CF14JT270R | Yageo | MFR-25FBF52-220R | TE Connectivity | CFR16J270R | Ohmite | OD271JE | Kamaya | RC1/4271JB | CF14JT270RCT-ND | 791-RC1/4-271JB | 148360 | 95W5736 | 2329504
R2; | 1 | Resistor 220 ohm 250mW through-hole | Stackpole Electronics | CF14JT270R | Yageo | MFR-25FBF52-220R | TE Connectivity | CFR16J270R | Ohmite | OD271JE | Kamaya | RC1/4271JB | CF14JT270RCT-ND | 791-RC1/4-271JB | 148360 | 95W5736 | 2329504
C1; | 1 | 100nF Capacitor Disc | Multicomp | MCFYU6104Z6 | KEMET | C052C104K5R5CA | KEMET | C052K104K5X5CA | KEMET | C052T104K5X5CS | KEMET | C321C104K5R5HA | BC1160CT-ND | 80C321C104K5R5HA | 852-3277 | 73M2154 | 2395773
J1; | 1 | CONN HEADER XH TOP 4POS 2.5MM | JST | B4B-XH-A (LF)(SN) |  |  |  |  |  |  |  |  | 455-2249-ND |  | 820-1551 |  | 1516278
D1; | 1 | 3mm LED any colour | Bivar Inc | ELM 5-065 | 492-2284-ND

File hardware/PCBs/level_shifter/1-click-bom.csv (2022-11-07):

References | Qty | Description | Manufacturer | MPN | Manufacturer | MPN | Manufacturer | MPN | Manufacturer | MPN | Manufacturer | MPN | Digikey | Mouser | RS | Newark | Farnell
J1;J2; | 2 | CONN HEADER XH TOP 4POS 2.5MM | JST | B4B-XH-A (LF)(SN) |  |  |  |  |  |  |  |  | 455-2249-ND |  | 8201551 |  | 1516278
J3; J4; J5; J6; | 4 | CONN HEADER XH TOP 2POS 2.5MM | JST | B2B-XH-A (LF)(SN) |  |  |  |  |  |  |  |  | 455-2247-ND |  | 8201554P | 73M9415 | 1516276
Q1; | 4 | 2N7000 |  |  |  |  |  |  |  |  | 2N7000FS-ND
R5;R6;R7;R8 | 9 | Resistor 1k ohm 250mW through-hole | TE Connectivity | CFR16J1K0 |  |  |  |  |  |  |  |  | A104669CT-ND | 279216239273 | 1251150 |  | 2329486
R11; | 1 | Resistor 560 ohm 250mW through-hole | TE Connectivity | CFR25J560R | KOA Speer | CF1/2CT52R561J |  |  |  |  |  |  |  |  |  |  |  | 2019-CF1/2CT52R561JCT-ND | 279CFR25J560R | 131227 | 2329690

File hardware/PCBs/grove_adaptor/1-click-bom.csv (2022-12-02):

References | Qty | Description | Manufacturer | MPN | Manufacturer | MPN | Manufacturer | MPN | Manufacturer | MPN | Manufacturer | MPN | Digikey | Mouser | RS | Newark | Farnell
J1 | 1 | CONN HEADER XH TOP 4POS 2.5MM | JST | B4B-XH-A (LF)(SN) |  |  |  |  |  |  |  |  | 455-2249-ND |  | 8201551 |  | 1516278
J2 | 1 | Grove male header | M5Stack Technology Co. Ltd. | A118 |  |  |  |  |  |  |  |  | 2221-A118-ND

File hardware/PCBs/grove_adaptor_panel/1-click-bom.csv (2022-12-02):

References | Qty | Description | Manufacturer | MPN | Manufacturer | MPN | Manufacturer | MPN | Manufacturer | MPN | Manufacturer | MPN | Digikey | Mouser | RS | Newark | Farnell
J1 | 12 | CONN HEADER XH TOP 4POS 2.5MM | JST | B4B-XH-A (LF)(SN) |  |  |  |  |  |  |  |  | 455-2249-ND |  | 8201551 |  | 1516278
J2 | 12 | Grove male header | M5Stack Technology Co. Ltd. | A118 |  |  |  |  |  |  |  |  | 2221-A118-ND

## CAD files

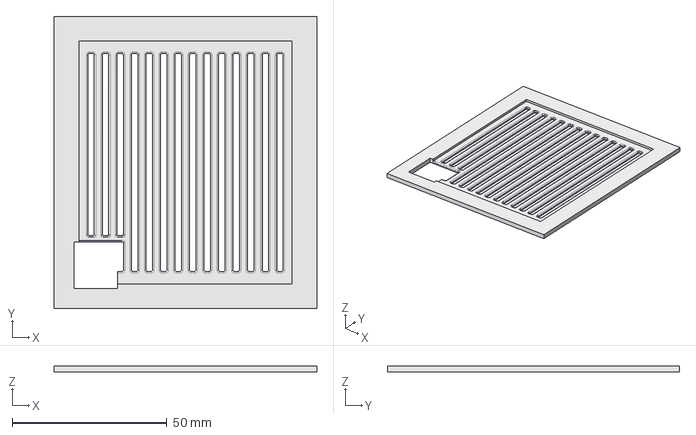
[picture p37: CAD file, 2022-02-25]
hardware/enclosure/front_panel_full_conn.FCStd
85.0 x 94.5 x 2.00 mm

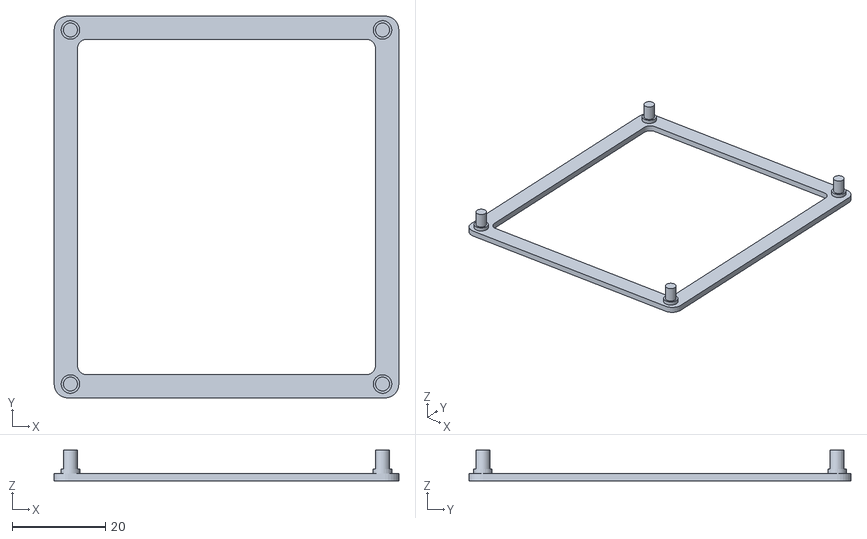
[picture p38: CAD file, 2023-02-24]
hardware/enclosure/pcb_holder/pcb_holder_v1_main_hub-BodyFillet001.stl
74.0 x 82.0 x 6.60

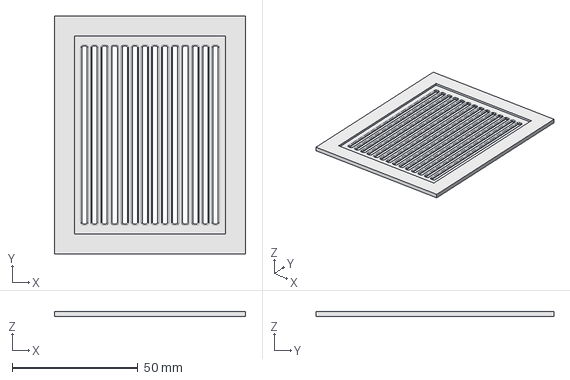
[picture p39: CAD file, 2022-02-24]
hardware/enclosure/side_panel_full.FCStd
76.0 x 94.5 x 2.00 mm

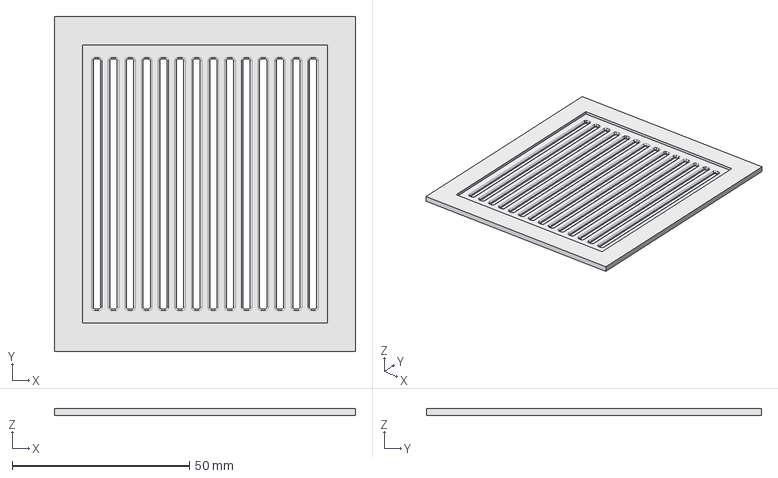
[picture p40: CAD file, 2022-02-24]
hardware/enclosure/front_panel_full.FCStd
85.0 x 94.5 x 2.00 mm

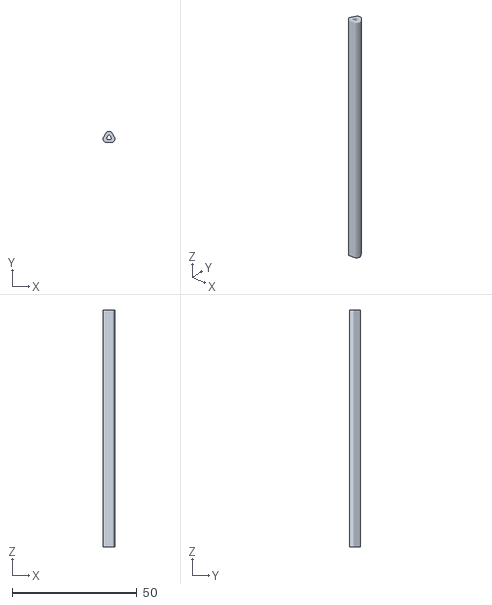
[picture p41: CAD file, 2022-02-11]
hardware/enclosure/main_support_v3-BodyFillet.stl
4.96 x 4.48 x 95.0

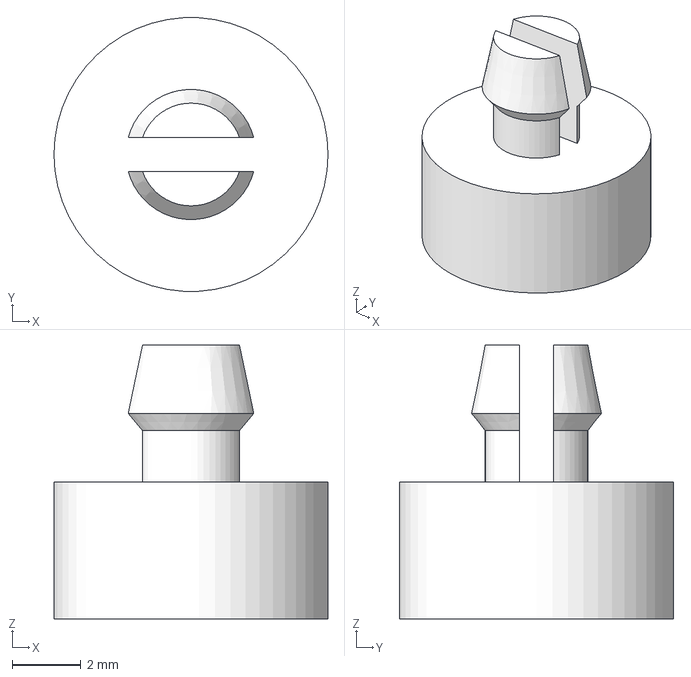
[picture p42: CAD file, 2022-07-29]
hardware/boards_spacer/spacer.FCStd
8.00 x 7.99 x 8.00 mm

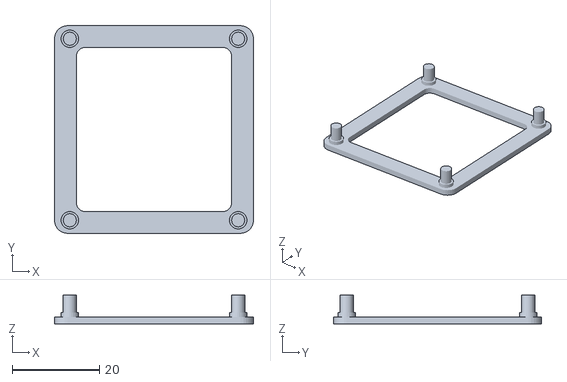
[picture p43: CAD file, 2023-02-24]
hardware/enclosure/pcb_holder/pcb_holder_v1_small_pcb-BodyFillet001.stl
45.5 x 47.5 x 6.60

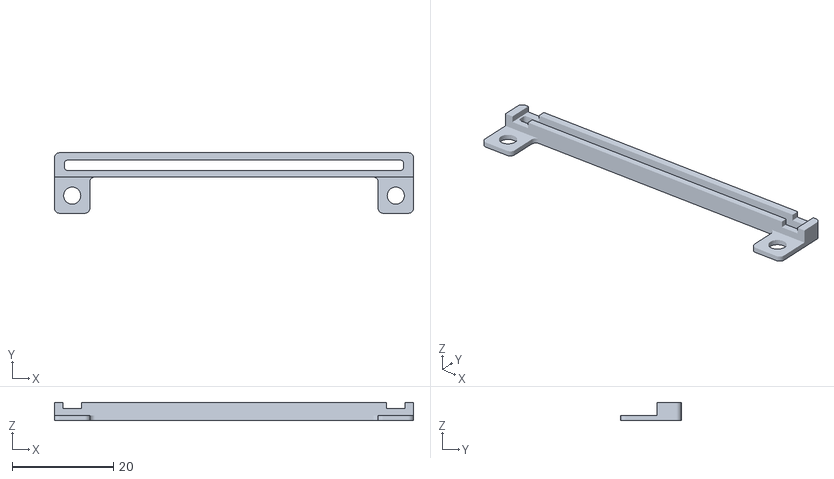
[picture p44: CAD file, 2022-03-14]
hardware/enclosure/slider_long-BodyPocket001.stl
71.0 x 12.0 x 3.60

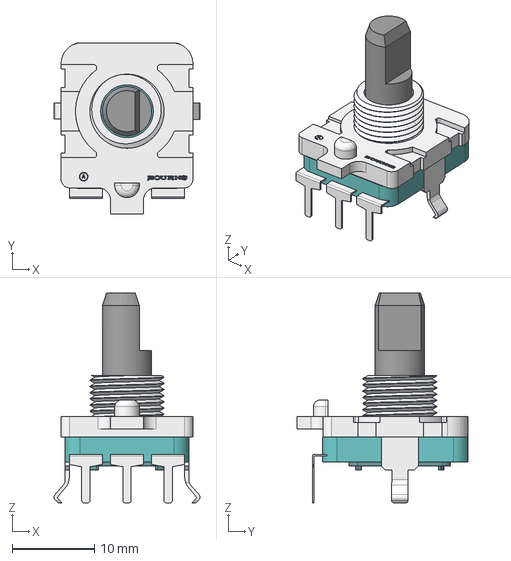
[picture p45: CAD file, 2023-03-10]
hardware/PCBs/training_board_v02/custom_encoder_footprint/eec.models/Bourns_Inc._-_PEC16-4015F-N0024.step
17.7 x 20.8 x 25.5 mm

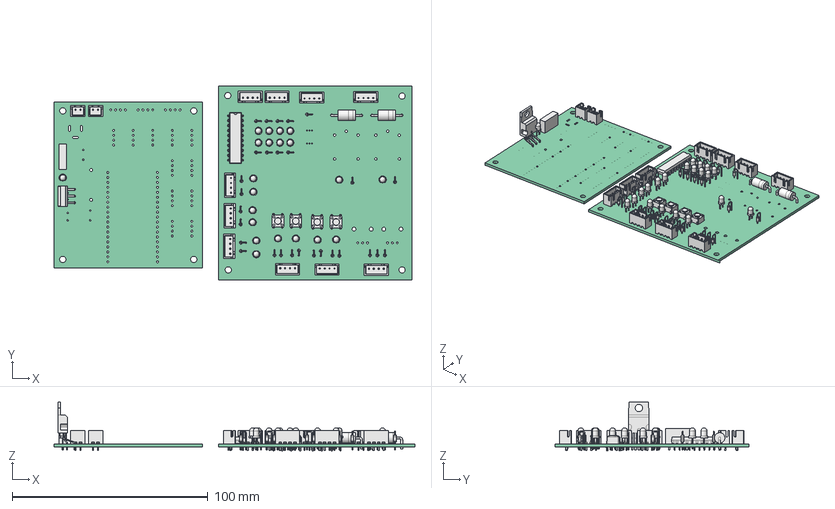
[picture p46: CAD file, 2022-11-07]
hardware/training_board_plate/enclosure.FCStd
184.6 x 99.1 x 24.9 mm
Pcb_b27c
P15_JST_B2B_XH_A_00005fd249f1 x 2
U1_TO_220_5_Pentawatt_Multiwatt_5_Vertical_StaggeredType1_000061e2f560
D2_LED_D3.0mm_000061ec0a3c
R1_R_Box_L130mm_W40mm_P900mm_000061ec0f77
Pcb_6084
D1_LED_D3.0mm_000061738582 x 20
J1_JST_B4B_XH_A_0000617386f0 x 10
R1_R_Axial_DIN0204_L36mm_D16mm_P254mm_Vertical_000061738945 x 28
SW1_SW_PUSH_6mm_000061738b22 x 4
U3_DIP-20_W7.62mm_000061e51c3a
D19_D_DO-201AE_P15.24mm_Horizontal_0000622f612b x 2

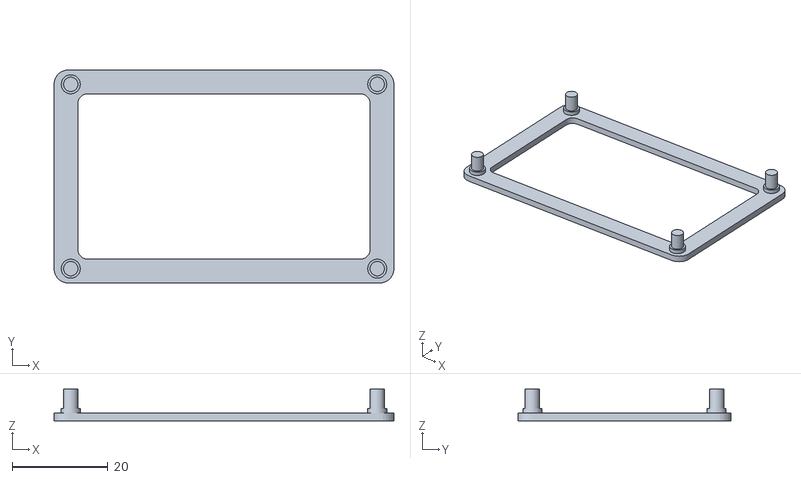
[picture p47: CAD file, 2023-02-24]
hardware/enclosure/pcb_holder/pcb_holder_v1_large_pcb-BodyFillet001.stl
71.0 x 44.5 x 6.60

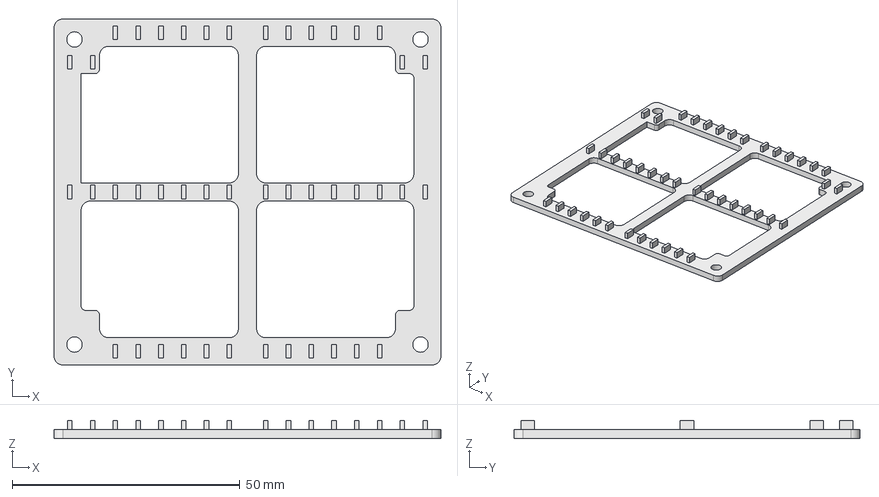
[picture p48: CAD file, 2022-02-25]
hardware/enclosure/pcb_cover_v3.FCStd
85.0 x 76.0 x 4.00 mm

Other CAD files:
hardware/enclosure/pcb_holder/pcb_holder_v1_main_hub.FCStd
hardware/enclosure/side_panel_full_conn.FCStd
hardware/enclosure/main_support_v3.FCStd
hardware/boards_spacer/spacer-Cut.stl
hardware/enclosure/slider_long.FCStd
hardware/enclosure/pcb_holder/pcb_holder_v1_small_pcb.FCStd
hardware/enclosure/base_v3-Pad005001.stl
hardware/enclosure/base_v3.FCStd
hardware/enclosure/hook-Body.stl
hardware/enclosure/hook.FCStd
hardware/enclosure/internal support_v3-BodyPad001.stl
hardware/enclosure/internal support_v3.FCStd
hardware/enclosure/pcb_cover_v3-BodyFillet001.stl
hardware/enclosure/pcb_cover_v4-BodyFillet001.stl
hardware/enclosure/pcb_cover_v4.FCStd
hardware/enclosure/pcb_holder/pcb_holder_v1_large_pcb.FCStd
hardware/enclosure/slider-Body.stl
hardware/enclosure/slider.FCStd
hardware/enclosure/top_v6_logo-BodyPocket007.stl
hardware/enclosure/top_v6_logo.FCStd

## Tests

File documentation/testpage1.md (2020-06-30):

[M4x10 screws]:Parts.yaml#M4x10PanSteel
# Software installation

{{BOM}}

## Method

# setting up the ESP32

## The system runs on Micropython, so we need to install that on the ESP32 first.
Users can follow the recommendations from the [Micropython documentation](http://docs.micropython.org/en/latest/)

software packages needed:
- esptool (install with pip)
- ampy (install with pip)
- rshell (instlal with pip)
- repl 

Here are the steps we took, running on Ubuntu 20.04:

note: On Linux, serial ports are described as something like `/dev/ttyUSB0`, in windows, they would be something like `COM4` (the number will change depending on computer, where usb was connected, etc). So make sure to change the commands listed below, depending on your operating system and serial port being used.

1. install esptool and erase current firwmare to start with a "clean board"
1.1 install the esptool, so you can write, erase firmware on the ESP32: `pip install esptool`
1.2 erase flash by running: `esptool.py --port /dev/ttyUSB0 erase_flash`

2. write the micropython firmware to the board:
2.1 run: `esptool.py --chip esp32 --port /dev/ttyUSB0 write_flash -z 0x1000 ~/Downloads/esp32-idf3-20200108-v1.12-44-ge3187b052.bin` where "~/Downloads/" is the path to where you downloaded the bin file

3. install Ampy, so you can upload files to the board, as well as download them into the computer: 
3.1 run: `pip install ampy-adafruit`
3.2 test ampy by listing the files on the board by running: `ampy --port /dev/ttyUSB0 --baud 115200 ls`
(this should return `/boot.py` (as this is automatically created when the firmware is written)

4. get the contents of boot.py from the board using ampy, so we can modify it (simply uploading a new file would also work fine):
4.1 get the file by running: `ampy --port /dev/ttyUSB0 --baud 115200 get boot.py`
4.2 copy these contents to a file named boot.py

5. upload your new boot.py to the board, making sure you are setting the location of the `boot.py` file in the command below.
5.1 run: `ampy --port /dev/ttyUSB0 --baud 115200 put boot.py` 
5.2 do this for the other files in your application.

With all files needed uploaded, we can connect to the serial interface of the micropython board and
run specific scripts, functions, etc.

6. install rshell: `pip install rshell`
6.1 Connect to repl using rshell `rshell --port /dev/ttyUSB0 --baud 115200 repl`
6.2 import and run your main.py script

This page should have some instructions for things in your project instead it just has a link for three [M4x10 screws]{Qty: 3} and another link to use [two more][M4x10 screws]{Qty: 2}.

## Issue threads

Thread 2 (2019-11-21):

BeeHive-org/BeeHive #2: General Purpose Hub and related project questions

isobianin, 2019-11-21:
The analysis of the current state of the scientific research tools, which are designated for microbiology, shows absence of the modular platforms used for defined subject area. The FlyPi project (https://github.com/amchagas/Flypi) contains valuable assets for the design of the new PCB hub that is supposed to maximize given modularity by means of different connectors. More information is given in https://github.com/amchagas/Flypi/issues/34

The design of this hub is closely related to the design of the each discrete module and should be kept in mind at all times. These modules allow user to customize the hub for specific research. It should be possible to connect other modules to given hub. Nevertheless, new modules should also be viewed as the less expensive alternative to the ones on the market. 

As the main microcontroller, ESP32 was chosen which is bound to increase effectiveness of the FlyPi v2 in an every aspect.

This issue is intended for the discussion of the hub itself as well as the discussion of all other related questions that cannot be answered in other issues.

isobianin, 2019-11-26:
Hi @amchagas !
I have been busy with academic tasks and have not yet severely touched this project. I have thought a lot things through. On the other hand, I will have a very difficult time for the next month (the master’s degree defense). Just wanted to say that I work on this but this work is very slow due to the parallel education process. Probably, I will have a bit more free time two or three weeks from now.

isobianin, 2019-11-26:
How many modules will we have? This parameter corresponds with the power supply. Maybe the power supply from the previous version will be sufficient. In case it will not be sufficient, some enhancements will be needed

isobianin, 2019-11-27:
I will follow my question with some ideas. I think that the main hub PCB should have an array of connectors (up to 10 but it may vary) and power supply (PS), which should have enough power to deal with 10 different modules. The trick here is that if somebody wants to have only 2-4 modules powered up simultaneously, the powerful PS may not be cost effective. However, I think that such small power ratings are not that big of a problem and we can place PS for 10 modules without much cost added (it still will be added but not like 10 times I suppose). The Raspberry PS probably should stay, however, I do not know for sure. 
What do you think, Andre?

amchagas, 2019-12-01:
Hi @isobianin ,
What about having a modular PS as well? as in the system has a PS for the main board and that is able to "juice up" some devices, but if users decide to plug something power hungry, they could attach an extra power supply in between the main board and the new attachment?

isobianin, 2019-12-02:
Greetings, @amchagas !
Yeah, I see it and really like the idea. I will try to come up with some ways of how it can be implemented in practice

isobianin, 2019-12-10:
Just a quick update. 
Basically, I am now experiencing the peak of an academic workload. I had some unforseen tasks due to the fact that I had done a very good project. It is going to be sent to the national competition of the student projects and there is a lot of paper work I am in right now. I am estimating that this week or the next one I will finally have time to make progress on the flypi project

isobianin, 2019-12-22:
Hi @amchagas !
I have made some progress related to the general design and now we have some new information to discuss.

The current design of the main hub PCB is shown below (fig.1). Dimensions and layout are subject to change but they show the most likely outcome of the design.
[image]
Fig. 1 - The general layout of the hub

The main hub have in total 13 connectors with 4 pins in each one. These connectors are:
- 8 digital general-purpose connectors
- 3 analog connectors
- 2 I2C connectors

Additionally, there is another connector that will link 12v line with the 5v modular PS. The power consumption in this case should not exceed adequate boundaries because the main PS 12v5a can maintain up to 50W (approximately 80% of the maximum of 12V*5A=60W). The modular PS (fig. 2) will have two connectors, just in case. I thought that it may be used solely for the LEDs but one extra connector may come in handy. Just to clarify, you have mentioned that there should be dedicated PS for powerful LEDs and this is not it, of course.
[image]
Fig. 2 - The modular 5v PS

Digital connectors will power almost every module and therefore there are relatively a lot of them. Analog connectors are reserved for sensors, which may have analog signal as the output data. I2C ports are placed just in case they may be needed.
Also there is a "switch" in the layout (fig. 1). I have placed it there so the user is able to test and/or use the circuit with one LED as in the original FlyPi. All other output connectors depend on the circuitry they ecnounter in the driving PCB and they should not be connected directly to LEDs or other stuff.
Speaking about LEDs, I have spent some time on the idea of shift register based hub (fig. 3).
[image]
Fig. 3 - The low power LED hub

The TPIC6B595 is able to provide current up to 150 mA to each of its pins. So it is able to power some low consumption LEDs with no problem. But they are still power hungry and that is why PS (fig. 2) is needed more than ever. There are two variants of the PCB with 4 or 8 LEDs.
This hub is controlled via 2 connectors from the hub (->ESP32) due to the fact that each connector provides 4 pins but shift registers needs 5. Particularly, it needs 3 data signals and GND/5V. We can place 5 pin connector but I doubt that it will be used for other devices (fig. 4).
[image]
Fig. 4 - 4 or 5 pin connector

There are more things I started working on but they are not polished yet for discussion.
To sum up,
1) Any concerns or propositions that are related to the main hub design? (general layout, connectors, modular PS and transistor switch)
2) The LED hub, what you think about this concept? And what about 4 and 5 pin connectors?

amchagas, 2020-01-06:
Hi @isobianin!
Sorry for the delay, went away for holiday break... 
Overall I like your idea with the main hub, modular PS and transistor switches. I think this provides a good "agnostic" main hub, so that we/others can add different things as needed. 

Is there any particular reason you are focusing on LEDs and different ways of powering/interacting with different LED formats (sorry if I missed this). Don't get me wrong, I don't mind start with LEDs, just wanted to know if there was any particular reason for it...

On a related note, I stumbled on this project https://github.com/RoboticsBrno/RB3200-ESP32universal/ which has somewhat the same idea I guess?

isobianin, 2020-01-07:
Hi @amchagas, I hope you enjoyed your holiday!
Understood, I am glad that the general idea is right and the development phase may continue.

Such focus on the LEDs is based on the fact that this kind of module is relatively simple to develop (imho) and we have not determined whether there are some high priority objectives. Also, I see that LEDs are practically an integral part of the laboratory setup in one or another form (regular LED or UV). On a side note, I feel that it will be easier personally for me to make something simple and then move to more complicated stuff. Such modules as Peltier are already implemented in the previous version and estimated to be quickly turned into the compact PCB when needed. 

You have found a very useful piece of information! I see we can draw some inspiration from this repository.

isobianin, 2020-01-17:
Hello @amchagas! Here is, finally, the first major update. Firstly, there is a schematics of the project (fig.1)
[image]
Fig. 1  - The FlyPi hub schematics
It is made as readable as possible. There are 8 digital connectors, 3 analog, 2 I2C, 1 UART (has been added in the last iteration of the project) and a connector to the additional power supply. ESP32 is represented by ESP32-DevKitC V2 board. It is powered by 5V voltage that is supplied to the corresponding pin. 
The pinout is also present in the figure and it is GND - VCC - DATA1 - DATA2. Such type of connection is common in electronics, especially in personal computers. Furthermore, Grove sensors and modules can also be connected to the FlyPi hub without any additional connectors.  
The aforementioned schematics is turned into the PCB (fig. 2).
[image]
Fig. 2 - PCB layout and tracks
This is the current version of the tracing. As for now, it does not have any vias, only though hole pads. Width of tracks are taken from the first version of the FlyPi and the track for 12V line is the widest (1.5 mm). 5V line and GND are zones on the each side of the board.
[image]
Fig. 3 - Dimensions
Figure 3 illustrates dimensions, mainly the fact that they are the same as before. Previously, although I 
had estimated that PCB would be approximately 10 mm bigger in the each direction, the layout was minimized to fit in the enclosure. USB port and barrel jack were moved slightly due to the fact that their positions play minimal role in the enclosure design.

Right now, I am trying to organize repository and create BOM is a such way that it is similar to the original FlyPi and it can be processed by Kitspace.

isobianin, 2020-01-17:
As far as I understand, until we have more PCBs in this repositry, Kitspace recognizes this PCB and show its render and BOM. As of yet, I have not created a project there but all the necessary steps are completed so it is not a problem (done with BOM). We only need to discuss the latest update

isobianin, 2020-01-20:
Currently working on the LED/transistor switch hub and the power supply

amchagas, 2020-01-21:
Hi @isobianin This looks great! 
As it is, it already makes for a nice tinkering/prototyping platform I think. 
I have two questions: 
Seems the ESP32-DevKitC V2 is already on V4, is there any particular reason why you choose this board to start things? 
Also, from the [documentation](https://docs.espressif.com/projects/esp-idf/en/latest/hw-reference/get-started-devkitc.html) it seems that this board also comes in different flavours... do you know if all of them would have the same footprint and if their pin out is the same?

isobianin, 2020-01-21:
Hi @amchagas !

About the devkit board. I have written that it is V2 but in the BOM V4 is used due to the fact that it is their latest version. Sorry, got too carried away and forgot to change/mention this.

The pinout of the devkit board is the same between the versions (V2-V4). The choice of the esp32 option depends on the computational requirements. The final pinout of the board with the given esp32 is the same across all the options ([ordering information](https://www.espressif.com/sites/default/files/documentation/espressif_products_ordering_information_en.pdf) page 11). Just in case, I have checked esp modules again and their layout is all the same. The footprint of the devkit board does not depend on the modules it is carrying and is invariable.

amchagas, 2020-01-21:
great thanks!

isobianin, 2020-01-23:
Hi @amchagas !
Finished the power supply module and the LED/transistor switch hub for 4 elements.
PS schematics (fig. 1) is the same as it is on the FlyPi board and have two output connectors as discussed earlier.
[image]
Fig. 1 - PS schematics
Its PCB is shown below
[image]
Fig. 2 - PCB of PS 
LED/transistor switch hub schematics is also present (fig. 3) and completely corresponds with our depicted design.
[image]
Fig. 3 - LED/transistor switch hub schematics
PCB will look like this (fig. 4). 
[image]
Fig. 4 - PCB for LED/transistor switch hub
All files are in the main repository. BOM have all the same components from the FlyPi except for the [shift register](https://ru.mouser.com/ProductDetail/Texas-Instruments/TPIC6B595N?qs=sGAEpiMZZMtsbn1GaJysl1mvuihK4f5q5rvouWD%252BBjQ%3D). 

For now, I am waiting for the prototyping results. During this time, I will design the transistor switch hub for 8 output devices and will look into other modules we agreed to develop. And one more important thing. I have mentioned it in amchagas/Flypi#34 that we will need some kind of enclosure for all this stuff. I would like to design it too as a part of this project if there is a possibility to test it out. Dimensions that are used in PS and LED hub are already lined up with my idea for the future enclosure.

amchagas, 2020-01-24:
Hi @isobianin,
this looks great! Some minor comments:
On your power board pinout, input and outputs have a different pin number to track configuration, and this is not wrong, but I think it would make life easier, since we are thinking about having different add on boards, if we decided on a convention for it. In other words, would it be too much trouble to have pin1 be Vcc and pin2 ground on all the plugs?

I know this may sound like too much detail, but I've caught myself a couple of times trying to debug issued on a board, and having a pattern to what was connected to what would have made things simpler. This will also make it easier when making different cables for the different boards as we will know that pins1 and 2 will always be vcc and gnd no matter what the board being connected to it is (of course when vcc and gnd are going to a certain board). 

One extra thing is that if Vcc is pin1 the square layout of that pin will match the square layout of the +pole on the capacitor and on the collector of the transistor. 

To help things move forward, should I make an order for this boards and test them? we are currently developing a behavioural box for some experiments and this would be a nice test bed for it!

isobianin, 2020-01-24:
Hi @amchagas , I see what you mean. In the end, we are designing this system for the purpose of being convenient to the user, particularly us. So we change pinout format to VCC-GND-DATA2-DATA1 across all the modules and the hub itself, right? Nevertheless, it will not take long. 

And one small thing, I thought that the main hub is good by itself but it may be even better if we go for 4 layer PCB (for the extra good EMC). Just a suggestion.

Considering boards, I think it is a great idea! As soon as the latest changes are implemented, I will notify you.

isobianin, 2020-01-25:
Hi @amchagas ! It is done, changes are implemented through all the PCBs. Also, I set up links to  screenshots of the current design of PCBs and schematics in the "README.md" so it is easier to monitor updates (probably).

amchagas, 2020-01-25:
Hi!
nice, thanks for the fast update! Quick question, on the main board image there seems to be an unconnected capacitor on the top right?

isobianin, 2020-01-25:
It is connected to the copper pours but, yeah, I missed this. I will manually connect them so the whole supply circuit can work properly
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

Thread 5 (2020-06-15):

BeeHive-org/BeeHive #5: Naming channels

amchagas, 2020-06-15:
At the moment, we used an "regular" naming convention of starting the digital channels from 0 upwards (and the same for the analog channels).

This makes sense, but makes it a bit hard to program the board, as these numbers do not reflect the IO of the board when calling functions.
Also, given the flexibility of each pin in the ESP32 (a digital pin, can be aslo a PWM, pin or an SPI, or a pin for a serial connection), this complicates things a bit.

I think it would make things more straight forward to name directly as their IO number, so for instance D0 would be IO33. A nice solution IMHO would be to keep the current numbering system, but add the IO reference next to it... (so something like DO/IO33) this way we can see straight away which pins can be used as analog, or SPI, etc. but still have an easy time programming things

isobianin, 2020-06-25:
Hi @amchagas!
I looked into this issue. I am inclined to agree that we better name the channels as they are in the ESP32. In order to safe the previous "regular" naming convention, we can have, say, IO31 on the front and D0 on the back of the PCB (fig. 1). It is double sided PCB and there should be no significant increase in cost. 

[image]
Fig. 1 - Combined naming on two layers

We may aswell try to stuff everything in a one text row but I fear that it may be unintelligible or it may not be printed at all (fig. 2)

[image]
Fig. 2 - Combined naming on one layer

If those variants do not meet expectations, we can always revert back to just IO ESP indicators without the current system.

amchagas, 2020-06-27:
Hi @isobianin 

From the two options, I think the first one is best (one writing on the back side). 

At the same time, now that I think about this again, I wonder if this is absolutely necessary? Is this nomenclature something needed for the board tracing/organization? 

Don't get me wrong, I don't mind keeping, it, I'm just wondering if having both wouldn't generate space for confusion?

isobianin, 2020-06-27:
D0...D(N) is great when working with some preprogrammed pieces of electronics but here it is, as our experience shows, a bit inconvenient. 
I believe that in our case we may in fact use solely ESP identification (like IO33, IO31). And I agree that less is more, especially with all the text that is up there on the PCB.

amchagas, 2020-08-19:
I think this issue is resolved. Mind if I close it?

isobianin, 2020-08-19:
Thought about it too, no problem, this is solved

closed 2020-08-20 by amchagas

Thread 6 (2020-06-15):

BeeHive-org/BeeHive #6: Update name on board and make ESP orientation explicit

amchagas, 2020-06-15:
Some cosmetic changes:
- Since we moved on from FlyPi V2, it would be nice to see this reflected on the board as well.
- Right now there is no information about the orientation of the ESP32 on the board. an easy fix would be to add some text saying "antenna side" and "usb side" or something like that....

isobianin, 2020-06-25:
Hi @amchagas !
I totally agree with this. And I also would like to put our new logo somewhere. **But** I saw something very unpleasant and we need to tackle it. 

Indeed, we need to have some kind of a text that suggests correct placement of ESP. And here is where the problem is. ESP32 is placed in a such way that its USB port is facing the wrong way (fig. 1). I thought that USB faces the other way so it is akin to the previous FlyPi design. But now it is what it is.

[image]
Fig. 1 - ESP32 orientation

The question here is simple, should we change the design of the layout and rotate ESP32 180 degree or leave it as it is?

amchagas, 2020-06-27:
hi, 
I thought that the orientation of the ESP was intentional! :)  as this way, the antenna of the system is a more "isolated" area, without signals that could possibly interfere, or be interfered with running below it. 

but I really don't know enough about wifi transmission and signal corruption to know if this is necessary when the board is "lifted up" from the PCB. 

If signal corruption is not an issue, rotating the board is a good idea, if not too much trouble

I also noticed that you might have created your own schematics and footprint for the ESP? I was just wondering if you knew about third party schematics/footprint repositories like this one https://www.snapeda.com/parts/ESP32-DEVKITC-32D/Espressif%20Systems/view-part/ This might be handy to facilitate derivatives? and I wonder if it would be useful to add it to BeeHive?

isobianin, 2020-06-27:
Regarding wi-fi electromagnetic compatibility (EMC) - it will be alright, there is nothing to worry. However, there may be changes in how ESP is connected to connectors. Of course, it is possible to rotate ESP and safe the current connections but it will create a mess in tracing and its EMC.

I will try to rotate it and come up with a new tracing. After that, we should look into it and decide whether it is worth it. I mean, we just need to see what the other option before discarding it.

Regarding footprints, I have just checked it and, in fact, I used this very file that you addressed. Indeed, we should add it.

isobianin, 2020-06-29:
Hi @amchagas !

Here is an update. First things first, there are major changes in the net list. Here is a figure of ESP32 connections (fig. 1).
[image]
Fig. 1 - New connections
And here is an old one (fig. 2).
[image]
Fig. 2 - Old connections

The new design features (fig. 3):
- names of pins are changed to "IO(N)" to ease programming;
- new logo is added;
- PCB is renamed to "BeeHive";
- orientation markers are added;
- UART connector (the arrow is pointing to it) changed its position to this location;
[image]
Fig. 3 - The redesign 

I hope it sums everything up. I will be waiting for further suggestions.

isobianin, 2020-06-30:
A table to structure changes and make reprogramming a bit easier.

Table 1 - The new pin mapping
| Connector pin | Old | New | Note |
| ------------- | ------------- | ------------- | ------------- |
| D1-3 | IO33 | IO15  | |
| D1-4 | IO32 | IO2  | |
| D2-3 | IO26 | IO0  | |
| D2-4 | IO25 | IO4  | |
| D3-3 | IO14 | IO16  | |
| D3-4 | IO27 | IO17  | |
| D4-3 | IO13 | IO5  | |
| D4-4 | IO12 | IO18  | |
| D5-3 | IO10 | IO19  | |
| D5-4 | IO9 | IO21  | |
| D6-3 | IO11 | IO22 | |
| D6-4 | IO19 | IO23  | |
| D7-3 | IO8 | IO14 | |
| D7-4 | IO7 | IO27  | |
| D8-3 | IO15 | IO26 | |
| D8-4 | IO2 | IO25  | |
| A1-3 | IO35 | IO35  | Unchanged |
| A1-4 | IO34 | IO34  | Unchanged |
| A2-3 | IO39 | IO39  | Unchanged |
| A2-4 | IO36 | IO36  | Unchanged |
| A3-3 | IO0 | IO32  | |
| A3-4 | IO4 | IO33  | |
| I2C_1-3 | IO0 | IO9  | |
| I2C_1-4 | IO4 | IO10  | |
| I2C_2-3 | IO16 | IO12  | |
| I2C_2-4 | IO17 | IO13  | |
| UART-3 (TX) | IO1 | IO1  | Unchanged |
| UART-4 (RX) | IO3 | IO3  | Unchanged |

amchagas, 2020-06-30:
Hi @isobianin 
this looks great! thanks for the update. 
I'll work more on some code these days and upload it here when it is in a good state.

amchagas, 2020-06-30:
related to #7 we should think about removing the "CC" mark from the board and add either CERN OHL license or TAPR, depending on which one we like best...
here is a more detailed explanation on hardware licensing https://opensource.com/law/15/2/intro-open-hardware-licensing

closed 2020-08-20 by amchagas

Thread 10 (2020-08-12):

BeeHive-org/BeeHive #10: Question about the 8 and 4 switch arrays NPN transistor connection

amchagas, 2020-08-12:
Hi @isobianin !

I was looking at the designs for the 8 and 4 switch arrays and I had a question (sorry I don't know if we cleared this before):

[image]

On the connections for the NPN transistor, shouldn't the transistor itself be connected to the ground line of the header pin, instead of the +5V?

In more detail shouldn't this be: +5V going to J3 1 and J3 2 being connected to Q1 1 and Q1 3 connected to ground?

isobianin, 2020-08-12:
Hi @amchagas !

No worries, we did not talk this through. This switch is done exactly as it was designed in FlyPi (Pic. 1)
[image]
Pic. 1 - NPN switch design
I thought that this design works in FlyPi and that the circuitry has already been programmed and tested. Thus, it was left as it is. If this type of switch needs redesign, we can implement your idea or think about something else.

amchagas, 2020-08-12:
oh, that was def. a design flaw on my side. It didn't lead to critical issues on the FlyPi design, but I correct it on a new update of the board I made (porting it to KiCad 5 mostly). I would correct that here as well if you don't mind... 

And sorry for the mistake that got propagated here!

best,
Andre

isobianin, 2020-08-12:
Got it. To be honest, I too let this discrepancy find its way into the new design. I will make the changes and post an update.

isobianin, 2020-08-16:
Hi @amchagas !
I have been redesigning PCB for the new layout with 74HC595 and noticed something in a circuitry. Mainly, I have connected transistors this way (fig. 1):
[image]
Fig. 1 - Common emitter
And you suggested to connect them this way (fig. 2) (maybe I have misunderstood your directions):
[image]
Fig. 2 - Common collector (?)
So do we use common emitter or common collector?
I believe that if we want to make a simple switch, we should refer to the first design with common emitter. I am not sure whether the second variant will work due to the fact that emitter in NPN-transistor is doped higher than collector. As alternative to the both schematics, we can use a voltage follower.

amchagas, 2020-08-16:
Hey, 

Yes you are right.  Figure 1  is the way to go. Sorry for the confusion!

closed 2020-08-19 by amchagas

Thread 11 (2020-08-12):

BeeHive-org/BeeHive #11: Question about power connector in 8 and 4 switch arrays

amchagas, 2020-08-12:
Hi @isobianin !
Another question related to these boards (sorry if it has been covered already!):

[image]

I was wondering if J1 1 and J2 1 pins should really be left unconnected? I see that the VCC for the shift register is coming from J11 but in this way the system is "locked" in 5V, I mean the shift register can only take up to 5.5V but we might want to use the transistor switches to switch, say 12V. so if the IC VCC comes from  J11, we can't use 12V. On the other hand if VCC to the IC comes from J1 and J2, then we use J11 to feed other voltages to the switch arrays?

Let me know what you think!
best,
Andre

isobianin, 2020-08-12:
I see what an idea is. It would be a great addition. Although, I am yet to think of an answer how to do it. I mean, if J1-1 and J2-1 are used as 5V, that means that 5V power is coming from ESP32 pins and I doubt that ESP will supply enough power, especially when the breakout is used for things other than lighting.

Actually, there are few things here I want to discuss. First of all, these switches were designed specifically for 5V (as you have mentioned, IC cannot pass more current/voltage than stated in datasheet). Secondly, it is envisioned that for high-power LEDs, a new board with completely separate power supply (12V/5A or more powerful) will be designed.

amchagas, 2020-08-12:
I don't know if I got this wrong, but I understand this system in this way:

The shift register just sends 5V out to the base of the transistors (so it is not high power), adding to that, the 5V coming from J1-1 and J2-1 are not coming from the ESP itself, but rather from the 5V regulator (using one of the LM2596) built in the main board (so there should be enough power for the shift register?).  

If this indeed works this way, then J11 is "free" for us to use with more flexibility, either 5V again from the LM2596 line or 12V from the 12V line. Since the transistors will be the only "connection point" between J11 and J1-1, J2-1 and this point will be the ground of both circuits, it should be fine to connect it this way?

isobianin, 2020-08-13:
Regarding J1-1/J2-1, you are right, my apologies.

Regarding 12V line, I see what you mean. If we are to take into account a new layout, it is certainly possible. Nothing restricts us from connecting 12V to the board (J11). So, in order to get things right, I will summarise:
- J1-1 or J2-1 will be used to power IC*
- J11 will be used to power transistors with 5V or 12V
*note: we could potentially power IC with J1-1 and transistors with J2-1 but when J11 is simultaneously connected, it will result in one of power supplies getting burned.   

This way, I will add dedicated power track for J1-1 or J2-1 to IC and power polygon will now be able to supply 12V/5V.

amchagas, 2020-08-13:
Great, thanks!

amchagas, 2020-08-13:
Hi, 
I am re-reading the datasheet for the TPIC6595 and now I see what you mean with the power LED  design. Since the pins of the shift register low-side open drains, so they shouldn't be able to "switch on" and NPN transistor in the config. I described, no? 
And if I understand correctly, in this new proposed configuration, we should not need the NPN transistor? Or is there a major missunderstanding from my side?

isobianin, 2020-08-13:
We may use LEDs without transistor solely with TPIC. But, if my hunch is correct, those transistors ([note](https://forum.arduino.cc/index.php?topic=112498.0)) were used to drive LEDs in order to lower current needed from pins (in FlyPi case, it was arduino pins). Here each pin can provide up to 250mA. With 12V addition, it is possible to drive even more powerful LEDs.

isobianin, 2020-08-13:
New design uploaded with "ver 2" affix in "hardware" folder

isobianin, 2020-08-14:
Hi @amchagas !
Are we going to make further changes to the design?

amchagas, 2020-08-14:
hi @isobianin,
Thanks for creating a new version so fast! 
So I took a look at the note you sent, but that seems like a bad example? I mean the schematics there seem wrong? from there, they also describe a different shift register, namely the sn74hc595. 

Looking at its [datasheet](https://www.ti.com/lit/ds/symlink/sn74hc595.pdf), specifically at point 10.2, it looks like this one has a different configuration from the  TPIC6595. Looks to me that the sn74.. is a "high side" shift register and the TPIC6595 a "low side" one? 

What I mean is that on the TPIC, setting any port of the device to "high" will simply open the internal gate and allow current to flow to ground. On the Sn74, turning any ports to high actually sends a voltage out of the device (as shown in the datasheet, point 10.2) that could actually be used to turn on an led, or forward bias another transistor.

If this is the case, then the current design for our 4 or 8 transistor switch is possibily not working as intended?

I don't know if I am getting this all wrong, sorry if I am, it is just that I never worked with this shift registers!

isobianin, 2020-08-14:
I see what you mean. Indeed, you are right and TPIC will not efficiently work that way. I am sorry that it turned out this way. With this in mind, it seems that we can design switches this way:
- replace TPIC with sn74hc595;
- use TPIC without transistors;
- use TPIC with transistors and think of a way of their implementation;
To be honest, when I had looked at the new transistors' placement, I immediately thought about going with 74HC595. My fault not seeing this before. How about we consider this option first? Are there any other ways we can improve on this design?

amchagas, 2020-08-14:
No worries! 
I think using the sn74hc595 is a good solution, it will allow us to be more flexible in terms of the transistors that can be used later on. I mean, if we need to change the transistors later, or if anyone else wants to derive this model into something else, they will also have an easier time changing it.

isobianin, 2020-08-18:
Hi @amchagas !
Both switches design is updated

amchagas, 2020-08-19:
Great, thanks! I'll look into making the boards and testing them etc..

isobianin, 2020-12-11:
Hi @amchagas !

Can we consider this issue closed? To summarise, here we implemented the following:
- making it possible to use 12V or 5V
- changed shift registers to the current ones

I believe that they were tested a long time ago, the issue is solved

amchagas, 2020-12-17:
indeed!

closed 2020-12-17 by amchagas

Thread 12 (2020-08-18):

BeeHive-org/BeeHive #12: Question about Peltier element

isobianin, 2020-08-18:
The previous installation of Peltier element has an L298N as a driver. The questions here are whether it is effective and are there any changes that need to be implemented? Also, there is a thermistor that is used to monitor temperature, any changes here?

Some background information. From what I have found out, the L298N can be controlled with PWM signals and that is exactly how it is done in FlyPi. However, there is a lost of efficiency when using pure PWM (a change between HIGH and LOW with different time intervals) due to the fact that this way Peltier is driven by current that changes from 0 to some max value. It is a problem because efficient cooling and heating of Peltier is achieved with current that is not 0 nor max value. Therefore, DC should be used ([note 1](http://www.rmtltd.ru/technology/tips/dc_or_pwm.php) and [note 2](https://electronics.stackexchange.com/questions/28634/how-to-drive-a-peltier-element)). It means that we need to control current flow either by filtering PWM signal or by a current regulator.

amchagas, 2020-08-19:
Having a temperature sensor + peltier element would be a great add to this system!
The way we developed things in the FlyPi was def. sub-optimal as it was all part of the first more "serious" interaction with electronics and as you mention there are a couple of things that could be done better:

- An analog temp sensor was used there, which is not a terrible idea, but that is quite prone to variance, depending on how the system is set, quality of solder, etc. Also it "blocks" an analog input port. I think this time around we would be better off using a sensor that outputs digital data? Something like the [ds18b20](https://docs.rs-online.com/bbac/A700000006834625.pdf) looks nice as it provides 0.5C accuracy over -10 to +85C range, and is transmits data over 1-wire protocol, so several can be used in the same data line. (But if you have other suggestions, let's chat about it!)

- As you mention we used the L298N, but as far as I remember, we mostly used it to flip current direction but always in full cycle, I don't think we used PWM with it. In any case, we also did a lot of cycling to keep the temperature at the desired state, which from the material you sent, is also not a good way to go. At some point it would be good to implement some code for PID control (maybe there are python libraries we can import to micropython)

- all this said, if you have the time to figure out a better way to implement the electronics for this, that would be much appreciated! :)

amchagas, 2020-08-24:
Hi!
I think that model is fine, as it was a 12V 5A model. That should be enough power for most applications I think. 
Related to this, we have been using these two things for a makeshift incubator: 
Temperature control https://www.aliexpress.com/item/4000773769510.html?spm=a2g0s.9042311.0.0.3b684c4dprTUIB
Peltier: https://www.aliexpress.com/item/4000216365780.html?spm=a2g0s.9042311.0.0.3b684c4dprTUIB

For the peltier we invert the wire connection so that instead of cooling down on the exposed side, it heats up.

The temperature controller is simply a relay system, and the power supply is just a regulated 12V 6A source.

Maybe this is useful for your research on the peltier drive?

isobianin, 2020-08-25:
Thanks @amchagas !

Of course, it is much appreciated and I will start implementing an idea soon

amchagas, 2020-08-25:
To be honest I have little knowledge about PID, so if you think the first option is good, let's give it a try!

isobianin, 2020-08-26:
Hi @amchagas !

Just to be on a safe side, is this **the latest** circuitry used for Peltier control?
[image]
I plan to modify it a bit. But if it was changed at some point, I hope to see how.

isobianin, 2020-08-27:
Hi @amchagas !

Here I have an important question regarding ESP32 and its PWM capabilities. From I what I could fathom, it should be possible to control PWM signal frequency and its resolution. Could we, according to [this](https://www.reddit.com/r/esp32/comments/cnpy5f/question_about_pwm_frequency_vs_bit_depth/), test a [code](https://randomnerdtutorials.com/esp32-pwm-arduino-ide/) in order to find out whether it is possible to run 8 bit PWM at 312500 Hz frequency? With the given there formula, we will have (2^bit_num)-1 = (2^8)-1 = 255 levels of attenuation (we can change Peltier heating or cooling intensity by 0,4%). With such high frequency, it is much easier to design compact and reliable LC circuit.

So, if it is possible, could you please test the aforementioned code with:
const int freq = 312500;
According to [wiki](https://docs.espressif.com/projects/esp-idf/en/latest/esp32/api-reference/peripherals/ledc.html), it will either result in an error occurring and nothing working, or it will work no problem. 

Maybe there are other ways of doing these but I can't seem to find accurate information regarding this question.

isobianin, 2020-08-27:
To sum up the previous comment, I think of an LC-circuit for PWM signal so we can regulate current through the Peltier element via change of PWM signal width. This method is commonly used in thermoelectric cooling and motor drivers because its energy losses are minimal. It is especially relevant in our system that is thought to function while feeding from a battery. With this design in mind, LC circuitry is best to be used at high frequency so individual elements are physically smaller, thus additionally reducing parasitic parameters. So if we are able to achieve frequency around "freq = 312500 Hz", it will be great. The PWM resolution is chosen for optimal attenuation. Nevertheless, we may change this when more information is be available. That is why I think it would be rational to test the hypothesis (referring to the frequency and its bit-ing interdependence) with simple LEDs or maybe find an answer in other ways.

isobianin, 2020-09-14:
It took much more time than expected. I will soon post an update with schematics and layout. Regarding the programming part, there are some news too that I hope to comment on later. Mainly, it is the PID algorithm in micropython

amchagas, 2020-09-15:
Hi @isobianin! Sorry for the long time gap. 
I'm returning from paternity leave today, and getting messages, emails and other admin stuff out of the way.

First of all, thanks for putting so much time and effort into this! Really appreciated.

Then some short answers:
Yes, the Peltier circuit is still that one indicated in your screenshot. 
I can test the board for the pwm today, both frequency and bit resolution.

isobianin, 2020-09-15:
Hi @amchagas, welcome back!
I am sorry, did not have an opportunity to answer promptly. Thanks for the information regarding Peltier. I am now (still) looking into / verifying some stuff. Just want to be sure that everything is thought through so we will have a working piece of equipment, minding that this one is crucial. Speaking about testing, it would be nice to hear results. This way we will know what our upper frequency boundaries are.

amchagas, 2020-09-16:
[image]
[image]

On the top right corner of the oscilloscope you can see the measured frequency.

So this works nicely it seems. Also the resolution is 10 bits! 
I took the notes from here, which are from ESP8266 but also worked on the ESP32

isobianin, 2020-09-16:
Great work! Speaking about the code, I will link one more project that I looked upon as the base of our PID algorithm. I have made there some comments but was not able to fully understand the code. And then I ran into H-bridge redesign process

amchagas, 2020-09-16:
cool, will you share everything here?

isobianin, 2020-09-16:
Yes, that will be the case

isobianin, 2020-09-16:
https://github.com/B3AU/micropython - the main inspiration for the PID algorithm. PID.py, PDM.py and main.py are of particular interest. However, these files are written for an old version of ESP8266. Some functions, like "import pyb" are no longer used so this code may not be the "out of the box" solution.
[Here](https://github.com/isobianin/BeeHive/blob/master/software/peltier/PID.py) lies the PID.py file with my additional comments. I think they may be helpful. Original file is [here](https://github.com/B3AU/micropython/blob/master/PID.py)
If my hunch is correct, [this](https://randomnerdtutorials.com/micropython-ds18b20-esp32-esp8266/) should be quite useful, because it is ESP32 code for data extraction from DS18B20 temperature sensor. I thought that there will be one such terminal for one temperature sensor on the Peltier driver PCB. And I have actually thought to add another module for DS where there is an array of block terminals for multiple sensors (around 6, perhaps) but not right now. Speaking of which, are we going to use 3 pin block terminal for it?

isobianin, 2020-09-21:
Hi @amchagas !

The Peltier [driver circuit](https://github.com/isobianin/BeeHive/tree/master/hardware/peltier) is finally finished (fig. 1). L1, L2 are taken straight from the power supply module. Hence, there is quite large margin for frequencies to be used. And yes, it is not as small and compact as it could be. On the other hand, it is easier to order lots of parts from one place (thus, there will be a discount) and with less variety in components values it is more standardized. But it may be tuned after prototyping results, if needed.
[image]
Fig. 1 - Circuitry

Circuit's working principle is quite simple. There are 2 inputs with 4 possible states (H-bridge). TC4420 driver puts HIGH or LOW signal according to its input (no inversion). PWM frequency can be more than 100kHz but it depends on the prototype testing results. There are two indicators of 12V and 5V lines (even though 5V line is used practically for temperature sensor only). MOSFETs used can be replaced with IRF4905PbF and IRFZ44NPbF (I found that they are quite common but cost more than the suggested ones). Regarding MOSFETs' temperature regime, they should work well without heatsinks. If we are to discuss shoot-through prevention, I suppose it can be solved via software means, mainly with a relatively long delay (1 sec should be more than enough) between polarity switching.

amchagas, 2020-09-23:
Hi!
Thanks for putting this together, it looks very nice!
I would not worry too much about footprint size now, nor the price of components for this one module. let's test it :) 

I agree with the idea that this would be used mostly with 12V.

About shoot-through, also I agree with adding a software delay should do the trick. We can document things and add "huge red letters" around it saying that users should be aware of reversing polarity.

I'll try to put an order for boards and components towards the end of this week so we can test this and the other updates.

isobianin, 2020-09-23:
Hi @amchagas !
I am glad that we have agreed on the design aspects. A note (warning) in documentation  sounds nice. 
I hope testing will go well.

P.s. I have gone through gas and humidity sensors and changed LED resistors' values

isobianin, 2020-09-23:
@amchagas While we are on it, I have a question regarding XH connectors, mainly their max current. Does it mean that we should change connectors that are leading to/going from 12V/5A power supply?

amchagas, 2020-09-28:
Hey, 
good catch.
I was thinking about possible solutions without having to redesign things, but none of them sound great:
a) use the spare pins on P15 of the central hub to make that port to be 12/12/GND/GND, in this way sharing the load to two wires for + and two wires for GND. This is a bit pushy, as each pin would still potentially get 2.5A, which is close to max rate. On the other connecting boards, we would than to switch each 12V input to 4 pin XH instead of 2 pin

b) Use a smaller power supply, maybe 12V and 3.6A, so this way, after some of the power is used by voltage converters and the ESP, we are below max rate. but this would be close as well. Could think of going even further down with the amperage of the power supply. This would also mean that potentially we would need a second power supply for things that draw a lot of power, like the peltier devices, stepper motors etc. 

c) change P15 an all other 12V pins to something that is capable of dealing with the current ratings. This is a bit annoying because it will require yet another terminal type (or simply solder the cables to the place where the connectors would be). But then again, this or a) sound like a more doable/safe solution?

isobianin, 2020-09-29:
Hi @amchagas ! 
I was thinking about an answer. In my opinion, we should take the c) approach with changing our connectors to the type that is suitable for 5A work. I believe, that it will not be that much big of a deal but what should we put there instead of JSTs? Terminals are one option but could we, say, use something along these lines:
https://uk.rs-online.com/web/p/pcb-headers/5355204/
https://uk.rs-online.com/web/p/pcb-headers/1800217/
https://uk.rs-online.com/web/p/pcb-headers/1643207/
To be honest, I cannot seem to find plastic connectors similar to JST ones and I think that connector type interface, that we have (had), is the best because it is easy to use and safe (it is actually why I am hesitant about installing lots of terminals)
How about aforementioned variants? What about terminals? What do you think?

amchagas, 2020-09-29:
Hey!

Are you thinking about replacing all connectors? or only the ones that are doing 12V and 5A? The reason I ask is that by removing all JST connectors, we lose GROVE compatibility, no?

I agree with you that the JST ones are nice since they have they only fit in one direction, and are easy to put together. 

Which is also why I considered just changing the 12V 5A connector (all the other ones are using maximally 3A from the 5V regulator, but if we are worried that this will be running on the edge, we can change the inductor value of the LM2596 to output max 2.5A), or using all 4pin JST connectors where we need to use 5A so that we have 2 wires for ground and 2 wires for V+, in this way splitting the total current in each pin?

isobianin, 2020-09-29:
I thought that we are talking about 12V5A line only and it is in our best interest to make the least amount of redesign. Particularly, I referred to 12V5A line connectors only, the rest of connectors should stay as they are.

Regarding the splitting idea, it sounds good on paper. Have you already tried this design trick? As for me, I am not sure that those pins will balance amperes equally. To back this doubt, I have not seen much PCBs and other projects where current is split in the way you described and there is probably a reason. But it may be just me.

To sum up, I agree with you on your idea to change only 12V5A line connectors or test whether 2 JST connectors can split the current. But even if they can, do we really have a guarantee that it will work okay when the setup will be used by other researchers?
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

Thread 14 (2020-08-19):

BeeHive-org/BeeHive #14: Making beehive GROVE compatible

amchagas, 2020-08-19:
Hi!

This is a bit of an annoying one but might be useful in the long run...

I was checking some boards at Seeed Studio for another board and realised that we the plugs we have are almost compatible with their Grove system, where they offer a lot of different sensors and actuators.

The main difference is that Grove uses a 4 pin system (same connector as ours I think), with 1 and 2 being "data" lines (digital or analog), 3 being VCC and 4 being GND 

This below is one example of a sound sensor plug schematic that only uses one data line. The sensor is this [one](https://wiki.seeedstudio.com/Grove-Sound_Sensor/)
[image]

I was wondering if it would make sense to make our system compatible, so that we gain access to all of these sensors/actuators "for free"? 

I know it will be a bit of a pain to re-order things, but maybe worth it in the long run? Also, I am happy to split the task so that we each take half the modules and update things.

What do you think?

amchagas, 2020-08-19:
actually [here](https://wiki.seeedstudio.com/Grove_System/) they have a whole description of the system with board sizes and pin mapping for digital, analog, i2c, etc

isobianin, 2020-08-19:
Hi @amchagas !

To be honest, it is a bit painful to see us coming back to this layout. Let me explain. On January 24 (check out our [general questions chat](https://github.com/isobianin/BeeHive/issues/2)) we decided to get away from GND VCC pinout because it was easier to debug. I apologize here for not backing up my decision but before 24 January pinout had been specifically made exactly the same with groove for the reasons you mentioned here (tested and cheap modules and there are a lot to choose from).

We may change the layout again, revert to what it had been before changes. On the other hand, can we just simply use wiring that has "free" headers-connectors? I mean, we can simply twist wires and connect "power" to "power" and "gnd" to "gnd" and data1 and data2 pins are the same. 

Generally speaking, I thought from the get-go that our system should be compatible with the closest analogous systems so I think it is wise to implement it, especially if we are remaining true to our open source policies. 

Regarding time, I think I can handle it and do it relatively quick because I spent lots of time recently redesigning switches and other sensors.

amchagas, 2020-08-20:
So sorry for this!! This is obviously my fault. For some reason I didn't realise that we were moving away from Grove!!! 

I can change the layouts, this way you don;t get the extra work for something that was on my end and you can focus on developing new circuits which are grove compatible? Just let me know, so that we are not both working on redesigning things

isobianin, 2020-08-21:
Hi @amchagas !

No worries, we will easily solve this discrepancy. Okay, I can focus on the other stuff. If there are any questions regarding PCBs, I am open for discussion

closed 2020-08-24 by amchagas

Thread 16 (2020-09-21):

BeeHive-org/BeeHive #16: High power LED driver

isobianin, 2020-09-21:
From what I was able to find, Grove has two modules which can be used with powerful LEDs:

- https://www.seeedstudio.com/Grove-LED-Strip-Driver.html

- https://www.seeedstudio.com/Grove-EL-Driver.html

However, they are relatively powerful. There are other examples that, probably, more appropriate:

- https://www.aliexpress.com/i/32993594548.html

- https://www.pcboard.ca/3-watt-pwm-star-led-driver

A long time ago, we determined that a high power LED driver should be present within BeeHive system. The question is, if we are to do it, what are the specifications for it? 
- Mainly, what LED(s) is it going to drive? It is highly likely that this question is related to a question whether is it going to be powered by 12V5A power supply or something new. 
- Should we use plastic JST connectors or terminal blocks for wires? 
- What about heat dissipation of an LED. Can it be cooled via heatsink or there are some specific requirements? What if an LED driver requires heatsink too? From the cost-effectiveness point of view, I think that we should try to omit anything that wastes energy and/or requires additional care/maintenance.
- How many high power LEDs are needed in the system simultaneously?
- How will an LED function in the system (where does it go and how is it going to be mounted there) and does it require any mechanical enclosure or something similar? I presume that FlyPi's solutions are applicable here.

amchagas, 2020-09-23:
Hi!
I am surprised that there are no more options on the Grove ecosystem to drive LEDs. Thanks for researching on this and for finding other options as well. 

I think we have too much of a loose concept on what are "high power leds". From experience what researchers call high power, is not necessarily what engineers would call high power ;) For biological applications, I think up to 3W leds should be more than enough.

I do not have very precise answer to your questions, but here is some direction:

1- I would stick to designs that can be driven by the 12V 5A power supply. If we need more power later, I would stick with 12V, but then get a power supply that has more amps. 

2 - I would imagine the JST connectors should be fine, since they can take up to 3A (https://docs.rs-online.com/f25e/0900766b81357f2f.pdf), and I think we should be below that in most cases? 

3 - If we can manage with heatsinks/passive cooling only, that would be ideal.

4 - can't know for sure... Sorry. Maybe let's design something that takes one led per channel/digital signal control and rely on the shift registers in case we need many?

5 - the mechanical details on how these are going to be held can change a lot I think. 
I am thinking we can use them for the following: - fluorescence, optogenetics (both similar to flypi), but also to control "day/night cycles" in behavioural boxes and or incubators
I think there can be so much variability in here that spending time to design a holder now is not the best time investiment

Let me know if this helps, or if it only adds confusion? Maybe a simple opamp current driving design with the option for the user to change the output current would be a good place to start?

isobianin, 2020-09-23:
Thanks for the detailed answer. I got the gist. There are a lot of questions from my side because I want us to determine what characteristics should the module designed have. As far as I can tell, it is alright.

For the starting point, yeah, I will look up to opamp circuitry and some other variants. I will post updates as there will be an advance with the development.

isobianin, 2020-12-14:
Hi @amchagas !

I was looking into this issue lately. I think about developing the design based of the foundation of the peltier module. I looked up OpAmp circuitry that you had proposed but I see that it has some overcomplicated aspects for what is easily achieved by the said MOSFET drivers. Yet, we already saw the results of the MOSFET drivers and they are plausible.

Regarding shift registers, I think to make a simple circuitry with four switches for a start. To be honest, I don't think that we will even need more than that. The shift registers will be the same as in our previous BJT arrays. The circuitry will have 2 drivers for 4 MOSFETs and all the complementary components. That is how is it for now

isobianin, 2020-12-14:
Hi @amchagas , while I am on this topic there is one more thing. I think controlling these LEDs with PWM is quite effective. On the other hand, it is somewhat difficult task to achieve with shift registers as in this case we would need to constantly turn the snifter on and off with the given frequency.
A good question on this topic.
https://electronics.stackexchange.com/questions/110744/pwm-driven-led-array-over-a-shift-register
There are libraries for 74hc595 registers for Arduino that do exactly this. Will it work or should we just connect IO pins directly to the drivers? There are also timer ICs like 555. I feel that we need to decide what approach we should take before commencing further development (I will just design only those parts of schematics that I am adamant about)

amchagas, 2020-12-17:
hum, this is an interesting question. maybe as an straightforward approach should we just connect the driver directly to the IO pins? there should be enough for the number of LEDs that might be needed in biological applocations, and we can use the shift register for other devices?

isobianin, 2020-12-17:
Hi @amchagas ,

precisely what I was thinking and referring to. Simple yet functionally complete and easy to program

amchagas, 2020-12-20:
👍 Great!

closed 2021-05-28 by isobianin

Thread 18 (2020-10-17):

BeeHive-org/BeeHive #18: System power management issue

isobianin, 2020-10-17:
Work on the Peltier driver design showed that the BeeHive system has some flows in regard to its power management system that is currently implemented (fig. 1). To put it simply, there was a strange feeling that something is not right in a way all the cables are connecting and, sadly, it turned out to be true.

[image]
Fig. 1 - Current power management system

As seen in the figure, the system cannot work as intended. Although it can be modified "on-site" but it is not the way it is supposed to be.
 
To be precise, 12V5A line is simultaneously represented by 4 pin connector (main hub and 5V power supply) and 2 pin connector (newly developed Peltier driver and 12V5A breakout). It is a 100% design issue and must be tackled. This issue leads to another one where 4 and 8 switch arrays cannot be fed with 12V5A line from the main hub because the connectors are different.
Those issues can be dealt with in 3 ways:
1) the least amount of redesign - we change 4 pins to 2 pints only on hub and 5V3A PS. Actually, it can be done even with the current version where on a place of 4 pins we solder 2 pin connector
2) the moderate amount of redesign - we change the whole 12V5A line to 4 pins because it is better from a standpoint of a current management. Even so it has its own flaws discussed in #12, I believe that it is indeed a good idea that actually was partially implemented a long time ago (the main hub has 4 pins for 12V5A). **The pinout in this case is** + + GND GND. In the same time, every module shown will have some changes.
3) a safe ideal variant - change 12V5A to 4 pins but with a new connector like [this](https://www.google.com/url?sa=i&url=https%3A%2F%2Fmy.rs-online.com%2Fweb%2Fp%2Fpcb-headers%2F3922565%2F&psig=AOvVaw0NDKhZTodLV2axwVmPIEX2&ust=1603025021242000&source=images&cd=vfe&ved=0CA0QjhxqFwoTCPCnxdzTu-wCFQAAAAAdAAAAABAJ). It is the most difficult variant yet it will be the safest as 12V5A line will be distinctive from all other lines. To think of it, maybe this variant can be implemented as _a user experience feedback_.

Another issue to mention is that I, unfortunately, slipped up and the **Peltier driver** has the **reversed pinout** as well as 12V5A, temperature and gas sensors. I am already onto this.

I will redo this stuff but we just need to decide what is the best way of power management. In my opinion, we can do it this way: take the 1) option and then look for option 2) and 3) after the field test.

isobianin, 2020-10-17:
A little update, it turned out that temperature/humidity and gas sensors are all alright, they had an old silk layer with wrong names for pins but the pinout is traced correctly

amchagas, 2020-10-22:
Hi @isobianin, 

Thanks for raising these issues! I have ordered a couple of boards that have these footprints and connectors, so I would suggest that I put them to use, test and report. This way we can cover these issues and if more issues arise while I am testing things, we can tackle all of them at once?

Also this will be a nice pressure for me to get things going on my side with software and task implementation!

isobianin, 2020-10-22:
Hi @amchagas ,

I think tackling all issues at once will be a nice way to do it. Sorry that we have to "debug" all of these, especially some very simple mistakes, using the real prototypes in the first place.

isobianin, 2020-12-11:
Hi @amchagas !

Today, I realized a comprehensive update on this issue. Most of the modules were quite easy to update. I was also able to fix some small things along the line. The peltier module can now be equipped with heatsinks and it has two connectors for 12V5A power lines. I guess this issue can be closed after testing. More detailed update log is in the 'description' of the 'summary'.

amchagas, 2020-12-17:
Hi @isobianin !
Thanks for the update! 
I am going to start end of the year break, but will order the boards so that they are here once I get back to test things and get it going.

closed 2021-05-28 by isobianin

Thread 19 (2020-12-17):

BeeHive-org/BeeHive #19: Shift register on 4 output signals boards

isobianin, 2020-12-17:
Questions have arisen while working on a high power LED switch array. It is highly likely that such array have a sufficient number of LED outputs which is 4. Therefore, the questions are:

1) Why bother with shift registers and addition of software libraries (referring to [this](https://github.com/isobianin/BeeHive/issues/16#issuecomment-744390693) comment), if an array board takes 4 pins from ESP32 regardless whether they operate a shift register or directly connected to drivers?
2) Could we omit a shift register on 4 switch array as it seems that it only adds unnecessary cost and complexity to the board? In FlyPi schematics, the given transistors worked fine while being directly controlled by Arduino pins.

amchagas, 2020-12-17:
interesting. Is your idea just having an 8 pin shift register and scrap the 4 pin one?

isobianin, 2020-12-17:
Hi @amchagas ,

not exactly. My idea is to get rid of a shift register (component) so the 4 switch array has no over-engineering. I believe that it is still an important asset as it will be relatively cheap and simple device while more complicated one (8 switch array) will have more outputs to offer

amchagas, 2020-12-20:
Hi!
Ah ok, I see. Indeed that makes a lot of sense. I would go for that (removing the shift register altogether).

isobianin, 2020-12-21:
Made these changes in the latest update and moved the previous version (ver 3) to the "archive"

closed 2020-12-21 by isobianin

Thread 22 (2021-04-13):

BeeHive-org/BeeHive #22: upload boards to kitspace

amchagas, 2021-04-13:
Hi @isobianin !
As I am about to order components to solder some boards and send them out to you and Thomas, it would make it easier for me if we uploaded the boards to kitspace (so that I can order components with the 1-click bom extension).

Are you confortable with that? As in do we think the current boards are in a stable enough state to be uploaded?

isobianin, 2021-04-13:
Hi @amchagas !

I have been checking the boards and I think they are good to go, yet I would like to point out two things. First of all, we had some problems with the MOSFET switch. About 4 month ago I implemented changes to the board where I rearranged MOSFETs in way that they can be equipped with heatsinks. Actually, I changed almost the whole layout as I also implemented another connector for 12V5A line. The aforementioned board is still to be tested but I think it is going to be okay. Secondly, about 2-3 month ago I did a small revision of all boards. Apart from adding version number to each of them, I did some small changes like adding an LED to 5V3A power supply module, changed orientation of connectors to match Grove's ones, etc. Hope we will get good results from prototyping.

amchagas, 2021-04-14:
Hi,
thanks for the update on what was done to the boards!! 
I will test the ones that I added to kitspace and once we know both the kitspace synching and the boards work fine, I will add the remaining ones

closed 2021-04-14 by amchagas

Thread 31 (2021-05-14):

BeeHive-org/BeeHive #31: board suggestion: solenoid controller

amchagas, 2021-05-14:
For an [odour stimulator project](https://github.com/Sussex-Neuroscience/odour-stimulator), I created a board that delivers a "spike and hold" signal. This was based on the [schematic](https://www.theleeco.com/engineering/electrical-engineering/lee-solenoid-valve-drive-circuit-schematics/) offered by the company that makes the solenoid valves that we are using for that project. 

I would like to suggest to adapt the created board so that it works with BeeHive.
- Right now the board takes in 24V to drive  12V solenoid valve. If we want the BeeHive version of the board to have the same specs, we would need to add a step up regulator to the board, so that it would take the standard 12V from beehive, convert it to 24V for the spike period of the signal. 
- Other than that, we would just need to change the connectors in the current board, as the board, the way it is, already has inputs to drive 2 solenoids.

isobianin, 2021-05-15:
Hi @amchagas ,

I was quite puzzled with the statement "the board takes 24V to drive 12V solenoid". I looked into schematics that is provided by 
the manufacturer and that is present in your repository. Am I right in an assumption that solenoids in this system work the way described by the manufacturer in the first passage? (fig. 1)
[image]
Fig. 1
I think that this is it because otherwise it is quite hard to understand why we need to step up 12V to 24V to then step it down again to 12V.

Regarding the implementation, yes, I think your idea is right. I will look into how to implement step up regulator and change connectors

amchagas, 2021-05-15:
Hi Ihor, 
The figure/explanation you shared is why the board needs 24v to drive a 12v solenoid. From what I understand this could be applied to any solenoid, and not just the one from this specific manufacturer?

Therefore we could add this circuit to step up the voltage, and the odour stimulator then becomes beehive compatible/driveable.. (I wonder if there are any ICs that allow for either step up/down depending on a combination of resistors? - this would make it quite flexible, no?)

The other option would be to skip the step up and make sure we use lower rated solenoids.

Thanks for looking into this!

amchagas, 2021-05-15:
You can also see below how the signal driving the solenoid looks like.. 

[image]

isobianin, 2021-05-17:
Hi @amchagas ,

thank you for the information provided. I have been looking into this and I too think that the recommendations from the manufacturer could be applied to all solenoids, regardless of their origin (except those that explicitly mention that their solenoids cannot be used under these conditions).
Regarding the step up regulator, I would like to ask quite a simple question: what is the best outcome for us? My opinion is that if we need 12V solenoids and "spike and hold" signal then we will try to reach this goal rather than changing it to omit implementing drastic changes.

amchagas, 2021-05-18:
Hi Ihor, 
the advantage that I see is that by using 12V solenoids we can add this odour stimulator to the "portfolio" of tools developed with BeeHive. Also as far as I know, a lot of solenoids use 12V by default... (but this is from observing, and not actually researching things).

isobianin, 2021-05-18:
Hi @amchagas ,
based on the information you provided, I think we should stick to 12V solenoids. I will look into how to make a step-up regulator or what can be done with this issue. Right now, I am thinking about making a step up regulator as a discrete module and finding one that can be bought. What do you think? Are there any other things in the system that may require 24V (like motors, servos)? If not, than a step-up regulator on a PCB with solenoid driver seems as a rational idea

amchagas, 2021-05-19:
Hi Ihor, 
thanks for looking into this. It is hard to tell if we ever going to need 24V for other applications. I think we should aim for not needing that, but hard to say with 100% of confidence. 

At the same time, a step up as a discrete module is a good general solution, but I wonder how much current we would be able to get from the step-up circuit (as far as I understand in step up applications you end up with a higher voltage having to "sacrifice" current?) to make it useful for other applications? (I really do not know how much motors, servos that are running at those voltages would need in terms of current?). For the solenoids we are using, I know that they are fairly low current... 

Also, for the solenoid board, having an isolated step up would mean we take the 12V from the main board, step up to 24V (for the spike phase of the signal on the board) then step it down again to 12V (for the remaining of the signal) on the solenoid board, maybe that is a bit wasteful? But than again if it works, it should be fine, since having a generic step up solution might be best?

Another argument on the solenoid board, is that having an external step up would allow us to use the solenoid board with different types of valves... I mean, if we use a 6V rated valve, we do not need the external step up, and can simply use the step down on the board. this would make the signal be 12V in spike phase, than 6V for the rest of the signal (I hope this makes sense?)

I have no preference relating to this, and would go with what solution you think it is best!

isobianin, 2021-05-19:
Hi Andre,

thanks for sharing a detailed opinion on this! Truly, I cannot seem to find a middle ground here, though I am gravitating towards a discrete regulator more. Yes, regulators are all about converting one component of power, voltage or current, into another, but power will remain constant in every case (or rather, it can only change via decreasing).

isobianin, 2021-05-21:
Hi @amchagas ,

take a look at this [step-up converter](https://www.aliexpress.com/item/1005001266721719.html?spm=a2g0o.productlist.0.0.656d7118CGmXlN&algo_pvid=e9a4d3f1-05fe-4c2f-9c81-0a6182b63f83&algo_expid=e9a4d3f1-05fe-4c2f-9c81-0a6182b63f83-2&btsid=0b0a556a16215243280922697e41ae&ws_ab_test=searchweb0_0,searchweb201602_,searchweb201603_). In essence, it is what we need: it is relatively cheap, adjustable and is proven to work.
Regarding our own implementation of something along these lines, it is still complicated. I spend time investigating possible solutions. I am still unsure what approach to take so that will take time. Regardless, I think the module that I mentioned above is worth checking out.

isobianin, 2021-05-21:
Hi @amchagas ,

take a look at [this step-up converter](https://www.aliexpress.com/item/1005001266721719.html?spm=a2g0o.productlist.0.0.656d7118CGmXlN&algo_pvid=e9a4d3f1-05fe-4c2f-9c81-0a6182b63f83&algo_expid=e9a4d3f1-05fe-4c2f-9c81-0a6182b63f83-2&btsid=0b0a556a16215243280922697e41ae&ws_ab_test=searchweb0_0,searchweb201602_,searchweb201603_). In essence, it is what we need: it is relatively cheap, adjustable and is proven to work.
Regarding our own implementation of something along these lines, it is still complicated. I spent time investigating possible solutions, though I am still unsure what approach to take so that will take a while. Regardless, I think the module that I mentioned above is worth checking out.

amchagas, 2021-05-21:
Hi @isobianin , I think the module looks good.

maybe an approach would be to buy some of them, test them out with the system and make decisions from there? 
I think having some hands on experience with it could help more informed decision?

isobianin, 2021-05-21:
Hi @amchagas ,

well, it is certainly a good decision, provided there is a budget for it. Honestly, I think that they will come in handy in all sorts of projects

isobianin, 2021-05-26:
Hi @amchagas ,

I would appreciate if you were to take a look at [the solenoid board](https://github.com/BeeHive-org/BeeHive/tree/master/hardware/spike_n_hold) and [a discrete boost converter](https://github.com/BeeHive-org/BeeHive/tree/master/hardware/12_24_boost_converter). The only thing that I was not able to fully complete are BOMs. In the solenoid board, I did not change it at all and in a discrete converter I filled in all rows except for LM555. 
The boost converter looks like this (fig. 1):
[image]
Fig. 1 - A boost converter
The most important thing in it is that I tried to make booster from the components we already have and it worked. This is why both schematics have detailed descriptions how and which components can be changed.

Also, I almost forgot, solenoid board have a connector for 24V in case a user have a discrete converter (fig. 2). This way, there is no need to install other components. It can be additionally used to provide 24V as an _output_ from the solenoid driver but I do not know whether it can be used somehow.
[image]
Fig. 2 - 24V connector on the solenoid driver

isobianin, 2021-05-27:
Hi @amchagas ,

I have a question regarding coils that we are using. In the solenoid controller board you used coils that are much smaller than those that had been used in FlyPi board and later adopted by BeeHive. From both footprints I can deduce that they are not interchangeable. The question is, what inductor are we going to end up using? It would be convenient to have only one type of inductor across the system

amchagas, 2021-05-27:
Hi @isobianin,
the boards look good! and great idea implementing the boost with the parts we are already using!!

About the inductor, we should stick with the same model and footprint we are already using. The different one on the other solenoid board is likely an oversight from my side...

isobianin, 2021-05-28:
Hi Andre, 
splendid. I changed the footprint, should be fine now.

isobianin, 2021-06-02:
Hi @amchagas ,

I made some changes to the discrete module, mainly, I added another connector that can output 24V just in case there are multiple low amp 24V modules (fig. 1)
[image]
Fig. 1 - Two 24V output connectors

amchagas, 2021-06-28:
Boards are arriving this week for testing!

In the meantime, I was thinking about the input signal pins. 
Right now, they are 2X 2pin, with input and ground. To easy compatibility with the rest of the system, we could simply replace them for 1X 4 pins that is compatible with the connectors leaving the central hub.

I made the necessary changes and uploaded them as a pull request: https://github.com/BeeHive-org/BeeHive/pull/32

isobianin, 2021-06-28:
Hi @amchagas ,

have you looked into this thoroughly? I remember that we thought through a convention regarding high ampere signals, in particular, that where high amperes present, two connectors are used. On the other hand, not all applications require a lot of amperes, so we settled to have two connectors "just in case" but commonly use only one. If you are using boards right now and it is more comfortable to have 1X 4pins connectors then there should be a lot more changes across the whole system.
As an example, [the main board](https://github.com/BeeHive-org/BeeHive/blob/master/hardware/hub_PCB_redesign/beehive_PCB.png) should have two connectors for 2 independent 12V5A lines. Thus, it is possible to power more electronic devices rather than just using 1X 4pin conn. But again, it depends on how the board is _actually_ being used so if 1x 4pinn is more convenient so be it

amchagas, 2021-06-28:
Oh sorry I probably didn't express myself properly.. the connectors I am referring to are the digital signals that control the turning on/off of the rest of the circuit.. so they are normally low power 3.3v to 5v Volts

isobianin, 2021-06-28:
I see, no worries! I have just got a little confused over this

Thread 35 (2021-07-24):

BeeHive-org/BeeHive #35: 8 switch array voltage

isobianin, 2021-07-24:
Hi Andre,

it is related to [this issue](https://github.com/BeeHive-org/5-choice-serial-reaction-time/issues/1) from the rodent behaviour.

So the 4 switch array should work fine but I think 8 switch array has a little design overlook inside so I just want to double check on that with you so we are on the same page. Please, have a look at the schematics. The shift register is supplied with 5V and thus outputs 5V too.
[image]
The reason why it got my attention is that 4 switch array completely mimics what was done back in FlyPi where pins where directly connected to bases of transistors through current limiting resistors. The difference is that 4 switch array connects 3.3V to the base while 8 switch array connects 5v, or at least that is what I think is going on here. 

I do not think that it is right. Maybe transistors work fine but probably adding simple voltage divider will balance things out as 3.3V is more appropriate. I have checked the register's datasheet and see that it can take as low as 2V so we should be alright.

amchagas, 2021-07-27:
good catch! 

Maybe this won't be a problem for the transistor themselves, do I remember correctly that we are using PN2222 transistors in this design? If so, they are the same from the FlyPi and so the Arduino there, sends out 5V on its DO ports... All this at least from a electronics working point of view... But now that I write, you were probably already aware of that?! :see_no_evil: 

Now, do you mean that outputting 5V is not correct because the rest of the system is 3.3V?

isobianin, 2021-07-27:
Hi, thanks for clarification. To be honest, I got a bit confused in this one. So we were using 5V in FlyPi and now we are working with 3.3V. From what I see, it is not a problem here as this switch will work as intended. On the other hand, I think 4 switch array is not. I remember that I took the shifter out and just connected pins directly to base resistors so probably some alternations there will be needed

amchagas, 2021-07-27:
Now I am a bit confused :D .. I thought we had phased out the 4 switch array as it was not necessary, since we had the 8 switch one? As in, it is the same IC, so if one needs less pins, just leave some of the footprints in the board unpopulated?

isobianin, 2021-07-27:
That makes sense, though, we never actually talked about it :sweat_smile: . I thought that 4 switch array avoids paying more for the IC if someone just needs a basic switch. If we settle with the doctrine that 8 switch array is our only switch board, I think I am okay with that. We just need to evaluate this

amchagas, 2021-08-17:
do I have that wrong again, that the 4 switch array and the 8 switch array use the same IC? 
If they use the same, then the cost of buildiing an 8 X 4 switch array is not so big... if they are indeed different, what is the cost difference between them? Does it pay off for the added number of PCBs and parts list?

isobianin, 2021-08-18:
Hi Andre,
to quote our wiki:

[image]

What happens is that 4 switch array does not have the IC at all thus lowering the cost. If I am not mistaken, the shift register costs **about 1 dollar**, maybe a bit less which is relatively high. The idea was to omit it and use high/low signals from the ESP32 itself to do the work. To make it work, we need to change resistors we have now to ones with lower resistance.

On the other hand, I think 8 switch array is indeed more versatile and it is also much better protected as the level shifter also is responsible for handling any voltage spike and other shenanigans. 

I hope it answers your questions

amchagas, 2021-08-20:
it does, thanks! I still have the older 4 switch arrays with shift registers here... I think this is what got me confused!

closed 2023-03-16 by amchagas

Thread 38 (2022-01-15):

BeeHive-org/BeeHive #38: all boards review

amchagas, 2022-01-15:
as we use this system more and more, we would like to review all the boards. This comes to improve things, adapt initial development that took a different direction, etc.

Main board suggestions:
- [ ]  get rid of the 5V plane and make it into a trace
- [ ] remove the USB 5V supply and the second power conversion module

New board suggestion:
- [ ] create a 12 to 5V board that has a USB port as output (or adapt existing ones)

isobianin, 2022-01-18:
- [ ] [level shifter](https://github.com/BeeHive-org/BeeHive/tree/master/hardware/level_shifter) might need a Zener diode to properly convert 5V to 3.3V as of right now the output can vary depending on the load that is connected to 3.3V. On the other hand, if the level shifter is solely used with low loads aka ports of microcontrollers, it will work fine even as is

isobianin, 2022-01-18:
- [ ] [IR sensors array](https://github.com/BeeHive-org/BeeHive/tree/master/hardware/ir_sensor) absolutely needs at the very least a Zener diode in 5V to 3.3V line to function properly

isobianin, 2022-01-18:
So I think it would be nice to get some testing, I guess? If things work the way it is - I am fine with that. I do not want to overcomplicated something that works. The problem with voltage divider may arise in the following cases:
1) IR board is fully loaded with phototransistors. If every connection is used, it might happen that the voltage divider may not supply the given voltage because of the resistance that changed because of all the load. On the other hand, 5V that is being converted to the voltage divider in the first place is regulated, so it might work fine
2) Level shifter board should not have problems as is because currents are low. But can it be that there are problems when working on high frequencies?

I honestly think that in the level shifter scenario we can even use one of the pins as a voltage supply and omit voltage divider at all

isobianin, 2022-01-18:
Possible solution to 5V to 3.3V DC issue is https://www.mouser.co.uk/ProductDetail/STMicroelectronics/LD1117V33?qs=sGAEpiMZZMug9GoBKXZ75%252BNB3YkcECi9WejQbqCGDNE%3D

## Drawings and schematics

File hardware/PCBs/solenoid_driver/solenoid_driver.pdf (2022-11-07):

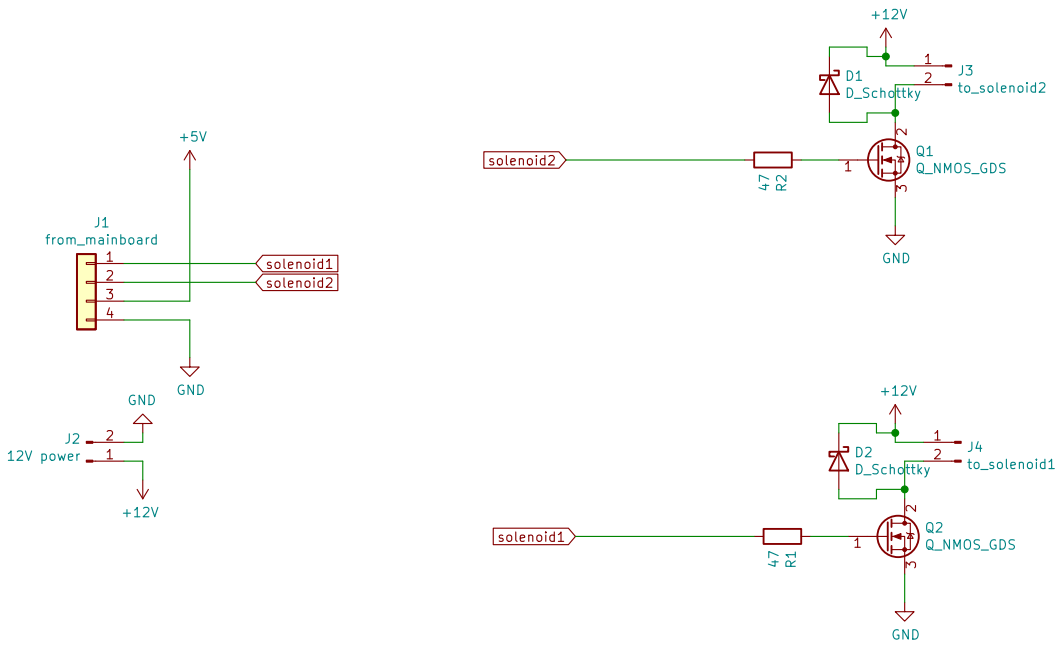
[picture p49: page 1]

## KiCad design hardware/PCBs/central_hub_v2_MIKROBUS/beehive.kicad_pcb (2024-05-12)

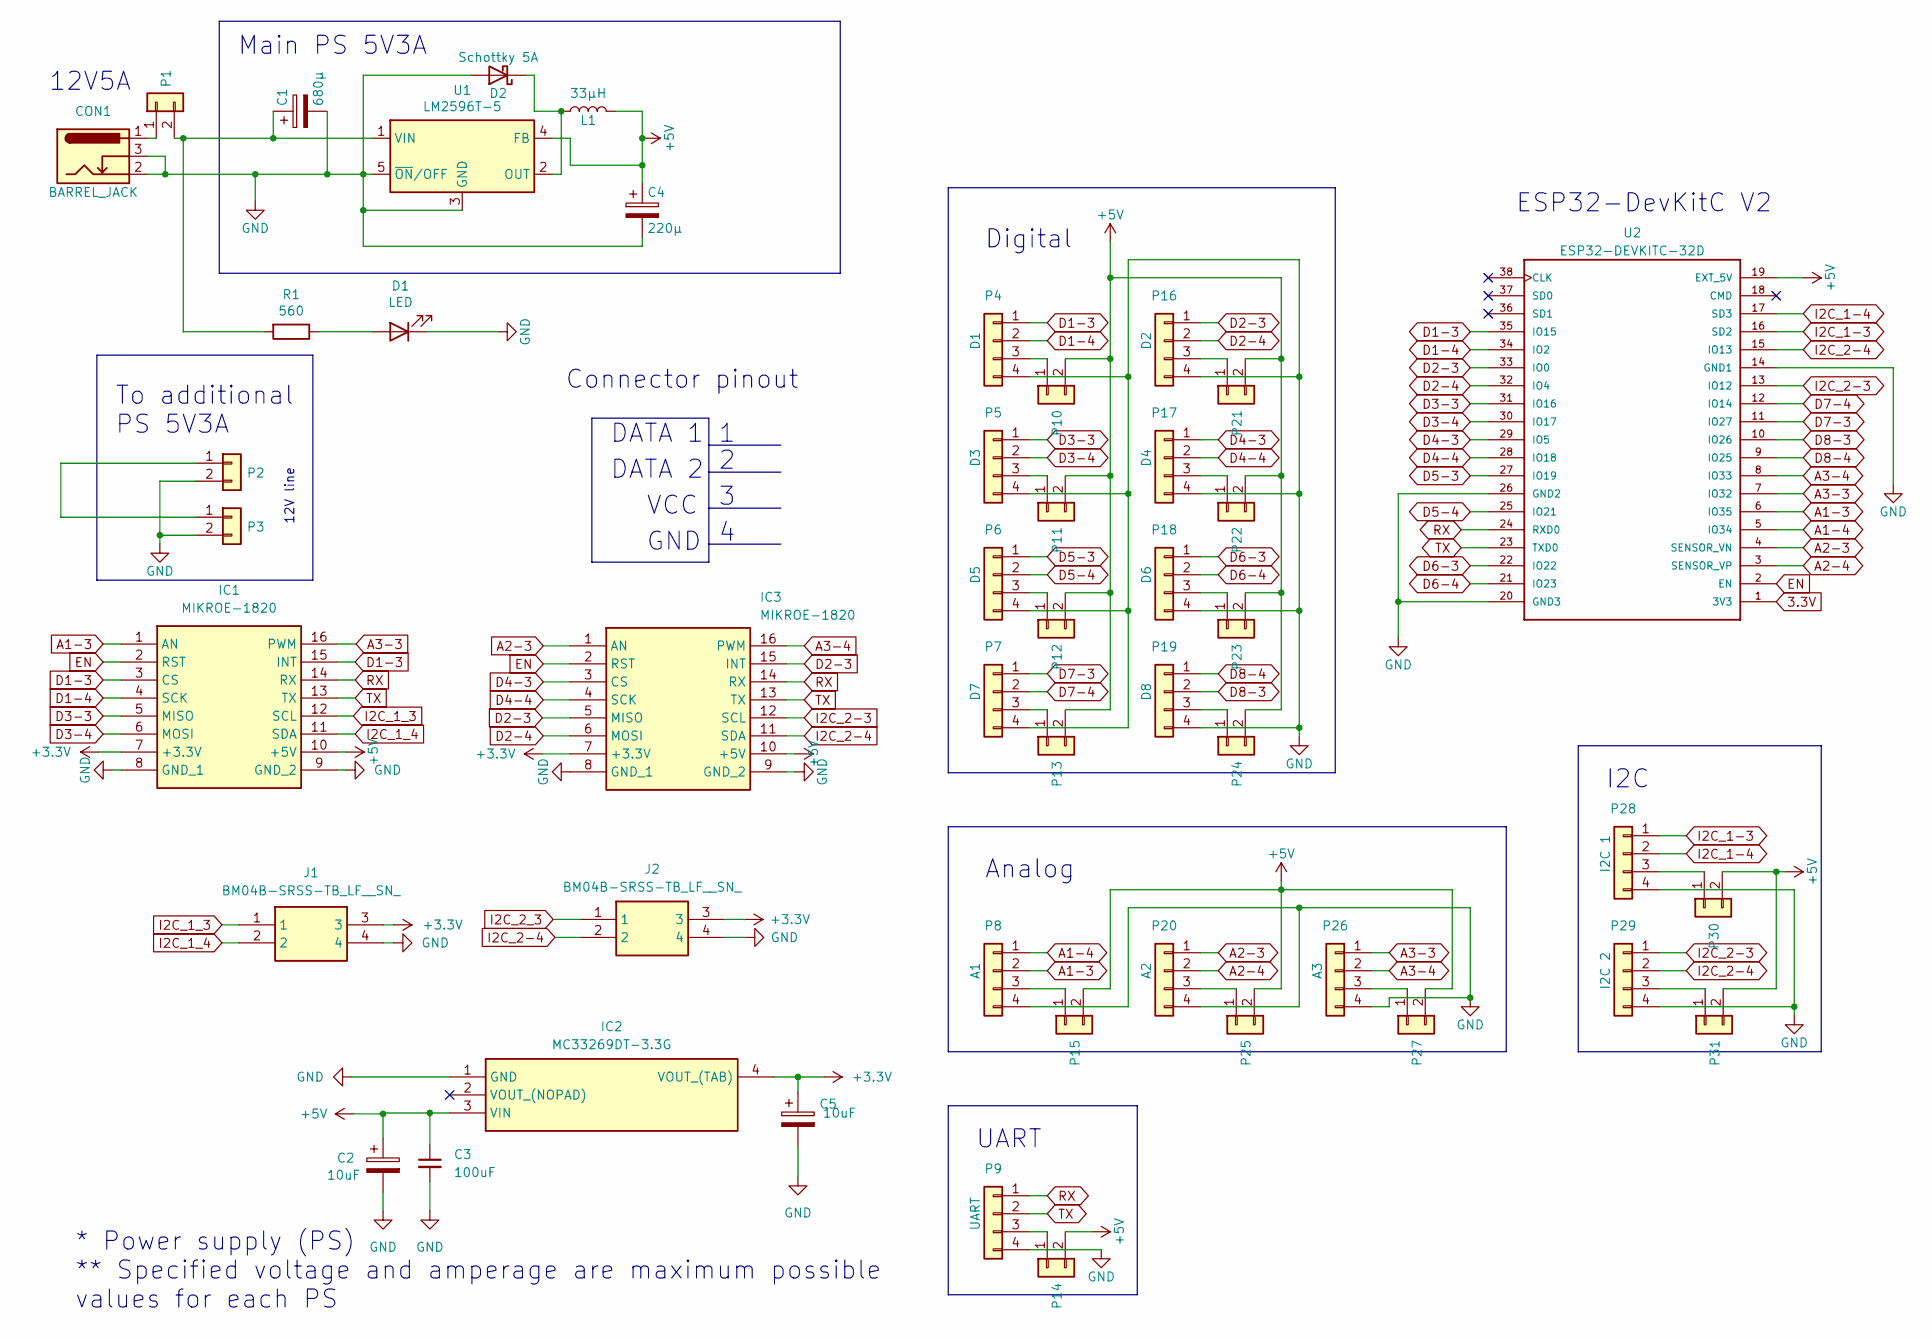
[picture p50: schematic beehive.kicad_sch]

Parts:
C1: 680µ; C_Radial_D10_L21_P5
C2, C5: 10uF; C_1206_3216Metric_Pad1.33x1.80mm_HandSolder
C3: 100uF; C_1206_3216Metric_Pad1.33x1.80mm_HandSolder
C4: 220µ; C_Radial_D8_L13_P3.8
CON1: BARREL_JACK; BarrelJack_Horizontal
D1: LED; LED_D3.0mm
D2: Schottky 5A; Diode_DO-201AD_Horizontal_RM15
IC1, IC3: MIKROE-1820; MIKROE1820; Mouser Part Number 932-MIKROE-1820
IC2: MC33269DT-3.3G; TO229P990X238-4N; Mouser Part Number 863-MC33269DT-3.3G
J1, J2: BM04B-SRSS-TB_LF__SN_; SM04B-SRSS-TB_LFSN_; Manufacturer_Part_Number BM04B-SRSS-TB(LF)(SN)
L1: 33µH; Neosid_Inductor_MA-Bs75
P1, P2, P3, P10, P11, P12, P13, P14, P15, P21, P22, P23, P24, P25, P27, P30, P31: Conn_01x02; JST_XH_B2B-XH-A_1x02_P2.50mm_Vertical
P4: D1; JST_XH_B04B-XH-A_04x2.50mm_Straight
P5: D3; JST_XH_B04B-XH-A_04x2.50mm_Straight
P6: D5; JST_XH_B04B-XH-A_04x2.50mm_Straight
P7: D7; JST_XH_B04B-XH-A_04x2.50mm_Straight
P8: A1; JST_XH_B04B-XH-A_04x2.50mm_Straight
P9: UART; JST_XH_B04B-XH-A_04x2.50mm_Straight
P16: D2; JST_XH_B04B-XH-A_04x2.50mm_Straight
P17: D4; JST_XH_B04B-XH-A_04x2.50mm_Straight
P18: D6; JST_XH_B04B-XH-A_04x2.50mm_Straight
P19: D8; JST_XH_B04B-XH-A_04x2.50mm_Straight
P20: A2; JST_XH_B04B-XH-A_04x2.50mm_Straight
P26: A3; JST_XH_B04B-XH-A_04x2.50mm_Straight
P28: I2C 1; JST_XH_B04B-XH-A_04x2.50mm_Straight
P29: I2C 2; JST_XH_B04B-XH-A_04x2.50mm_Straight
R1: 560; R_Box_L13.0mm_W4.0mm_P9.00mm
U1: LM2596T-5; TO-220-5_P3.4x3.7mm_StaggerOdd_Lead3.8mm_Vertical
U2: ESP32-DEVKITC-32D; MODULE_ESP32-DEVKITC-32D

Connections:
3.3V: U2.1 (3V3)
+3.3V: C5.1, IC1.7 (+3.3V), IC2.4 (VOUT_(TAB)), IC3.7 (+3.3V), J1.3, J2.3
A1-3: IC1.1 (AN), P8.2, U2.6 (IO35)
A1-4: P8.1, U2.5 (IO34)
A2-3: IC3.1 (AN), P20.1, U2.4 (SENSOR_VN)
A2-4: P20.2, U2.3 (SENSOR_VP)
A3-3: IC1.16 (PWM), P26.1, U2.7 (IO32)
A3-4: IC3.16 (PWM), P26.2, U2.8 (IO33)
D1-3: IC1.3 (CS), IC1.15 (INT), P4.1, U2.35 (IO15)
D1-4: IC1.4 (SCK), P4.2, U2.34 (IO2)
D2-3: IC3.5 (MISO), IC3.15 (INT), P16.1, U2.33 (IO0)
D2-4: IC3.6 (MOSI), P16.2, U2.32 (IO4)
D3-3: IC1.5 (MISO), P5.1, U2.31 (IO16)
D3-4: IC1.6 (MOSI), P5.2, U2.30 (IO17)
D4-3: IC3.3 (CS), P17.1, U2.29 (IO5)
D4-4: IC3.4 (SCK), P17.2, U2.28 (IO18)
D5-3: P6.1, U2.27 (IO19)
D5-4: P6.2, U2.25 (IO21)
D6-3: P18.1, U2.22 (IO22)
D6-4: P18.2, U2.21 (IO23)
D7-3: P7.1, U2.11 (IO27)
D7-4: P7.2, U2.12 (IO14)
D8-3: P19.2, U2.10 (IO26)
D8-4: P19.1, U2.9 (IO25)
EN: IC1.2 (RST), IC3.2 (RST), U2.2 (EN)
GND: C1.2, C2.2, C3.2, C4.2, C5.2, CON1.2, CON1.3, D1.1 (K), D2.2 (A), IC1.8 (GND_1), IC1.9 (GND_2), IC2.1 (GND), IC3.8 (GND_1), IC3.9 (GND_2), J1.4, J2.4, P2.2, P3.2, P4.4, P5.4, P6.4, P7.4, P8.4, P9.4, P16.4, P17.4, P18.4, P19.4, P20.4, P26.4, P28.4, P29.4, U1.3 (GND), U1.5 (~ON/OFF), U2.14 (GND1), U2.20 (GND3), U2.26 (GND2)
I2C_1-3: P28.1, U2.16 (SD2)
I2C_1-4: P28.2, U2.17 (SD3)
I2C_1_3: IC1.12 (SCL), J1.1
I2C_1_4: IC1.11 (SDA), J1.2
I2C_2-3: IC3.12 (SCL), P29.1, U2.13 (IO12)
I2C_2-4: IC3.11 (SDA), J2.2, P29.2, U2.15 (IO13)
I2C_2_3: J2.1
unnamed: D1.2 (A), R1.1
unnamed: D2.1 (K), L1.1, U1.2 (OUT)
unnamed: CON1.1, P1.1
unnamed: P2.1, P3.1
unnamed: P4.3, P10.1
unnamed: P5.3, P11.1
unnamed: P6.3, P12.1
unnamed: P7.3, P13.1
unnamed: P9.3, P14.1
unnamed: P8.3, P15.1
unnamed: P16.3, P21.1
unnamed: P17.3, P22.1
unnamed: P18.3, P23.1
unnamed: P19.3, P24.1
unnamed: P20.3, P25.1
unnamed: P26.3, P27.1
unnamed: P28.3, P30.1
unnamed: P29.3, P31.1
RX: IC1.14 (RX), IC3.14 (RX), P9.1, U2.24 (RXD0)
TX: IC1.13 (TX), IC3.13 (TX), P9.2, U2.23 (TXD0)

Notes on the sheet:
Connector pinout
12V line
To additional PS 5V3A
VCC
Analog
12V5A
DATA 1
GND
ESP32-DevKitC V2
Main PS 5V3A
* Power supply (PS) ** Specified voltage and amperage are maximum possible values for each PS
DATA 2
I2C
UART
Digital

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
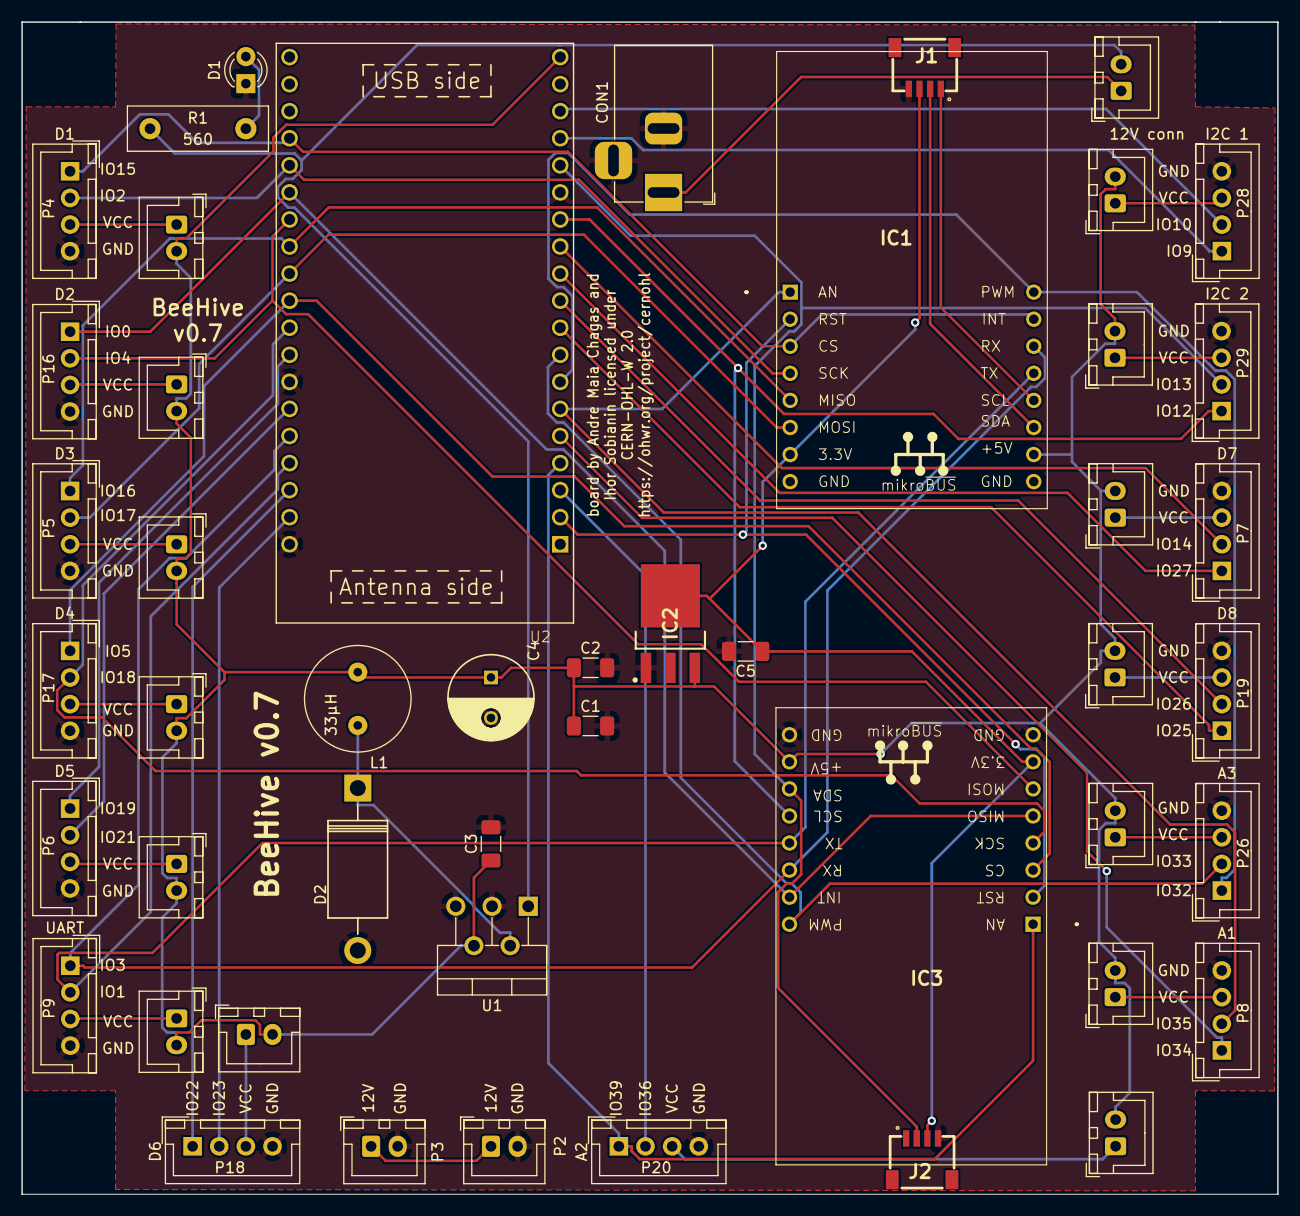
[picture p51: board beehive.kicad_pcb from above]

Board: 2 copper layers, 117.8 x 110.0 mm, 48 parts (0 on the bottom side), 53 nets.

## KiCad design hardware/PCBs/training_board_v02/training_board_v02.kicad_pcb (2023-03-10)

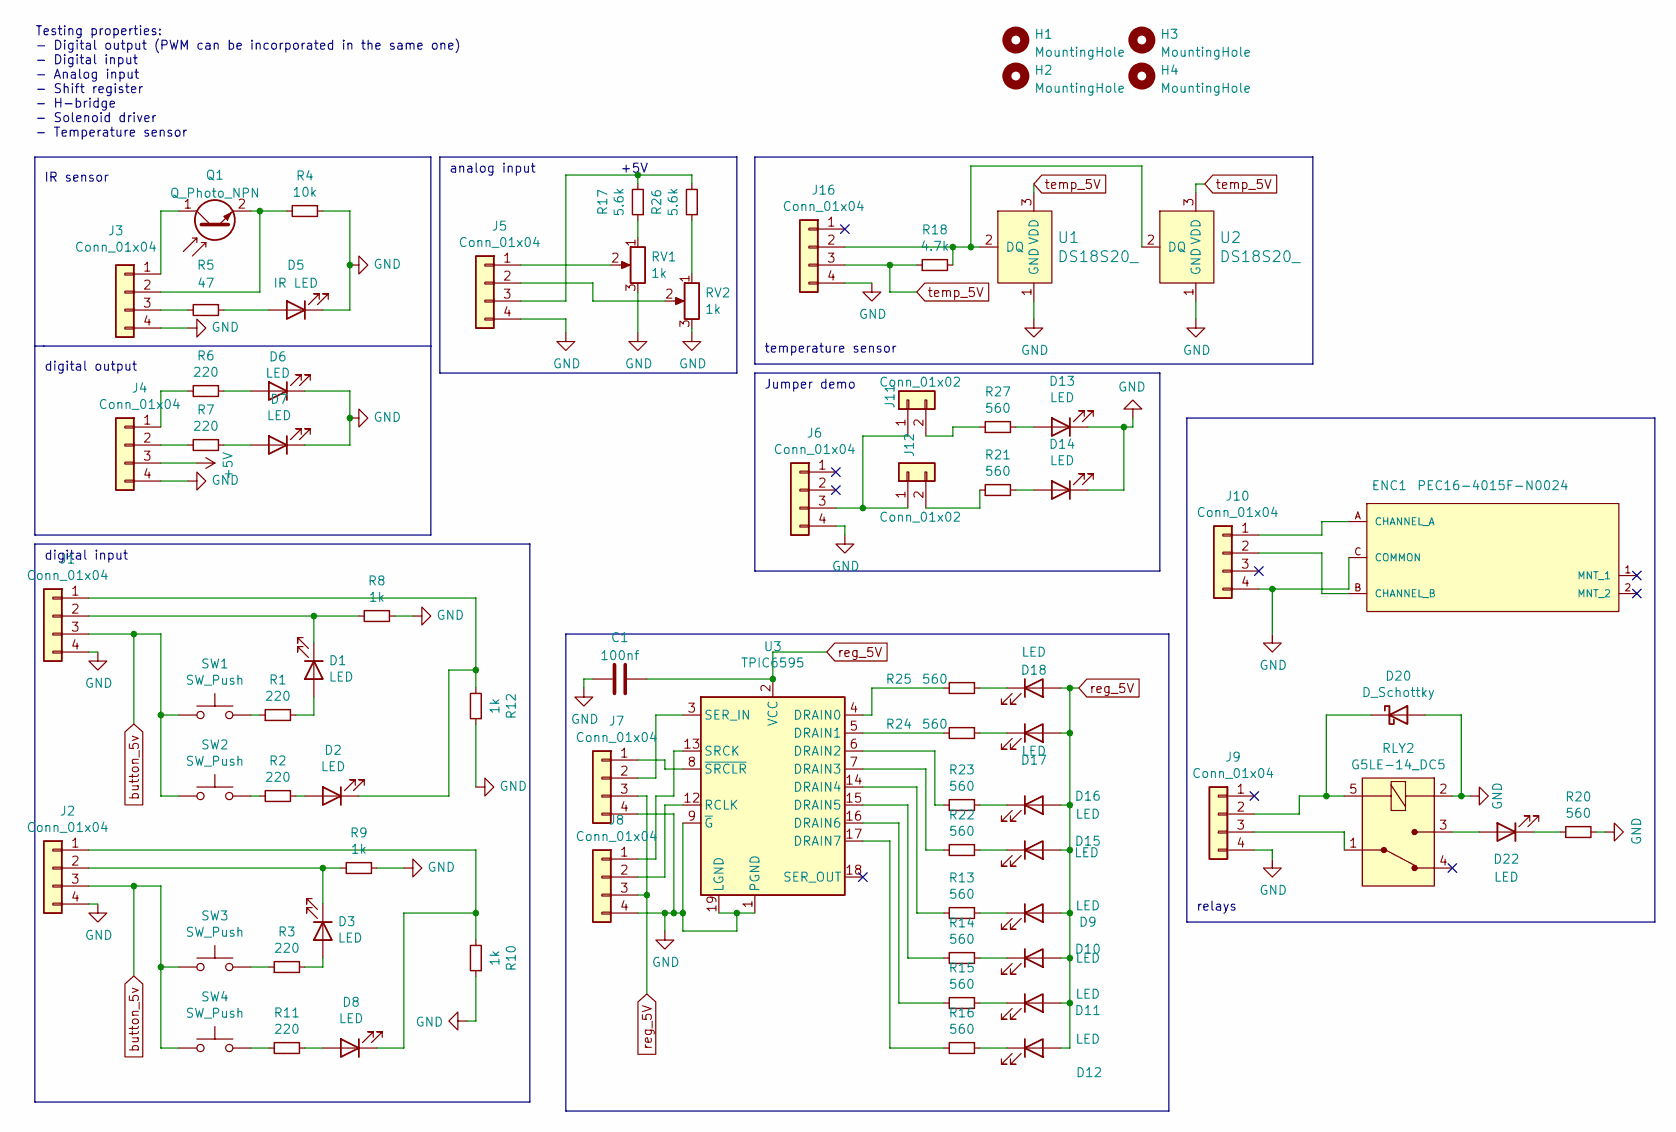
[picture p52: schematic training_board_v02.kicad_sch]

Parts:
C1: 100nf; C_Disc_D7.5mm_W5.0mm_P10.00mm
D1, D2, D3, D6, D7, D8, D9, D10, D11, D12, D13, D14, D15, D16, D17, D18, D22: LED; LED_D3.0mm
D5: IR LED; LED_D3.0mm
D20: D_Schottky; D_DO-201AE_P15.24mm_Horizontal
ENC1: PEC16-4015F-N0024; Bourns_Inc.-PEC16-4015F-N0024-MFG; current rating 1mA; voltage rating DC 5V; mouser part number 652-PEC16-4015FN0024; digikey description ROTARY ENCODER MECHANICAL 24PPR
H1, H2, H3, H4: MountingHole; MountingHole_3.2mm_M3_DIN965
J1, J2, J3, J4, J5, J6, J7, J8, J9, J10, J16: Conn_01x04; JST_XH_B4B-XH-A_1x04_P2.50mm_Vertical
J11, J12: Conn_01x02; JST_XH_B2B-XH-A_1x02_P2.50mm_Vertical
Q1: Q_Photo_NPN; LED_D3.0mm
R1, R2, R3, R6, R7, R11: 220; R_Axial_DIN0204_L3.6mm_D1.6mm_P2.54mm_Vertical
R4: 10k; R_Axial_DIN0204_L3.6mm_D1.6mm_P2.54mm_Vertical
R5: 47; R_Axial_DIN0204_L3.6mm_D1.6mm_P2.54mm_Vertical
R8, R9, R10, R12: 1k; R_Axial_DIN0204_L3.6mm_D1.6mm_P2.54mm_Vertical
R13, R14, R15, R16, R20, R21, R22, R23, R24, R25, R27: 560; R_Axial_DIN0204_L3.6mm_D1.6mm_P2.54mm_Vertical
R17, R26: 5.6k; R_Axial_DIN0204_L3.6mm_D1.6mm_P2.54mm_Vertical
R18: 4.7k; R_Axial_DIN0204_L3.6mm_D1.6mm_P2.54mm_Vertical
RLY2: G5LE-14_DC5; Relay_THT_G5LE-14; MPN G5LE-14 DC5; Digi-Key_PN Z1011-ND
RV1, RV2: 1k; Potentiometer_Alps_RK09K_Single_Vertical
SW1, SW2, SW3, SW4: SW_Push; SW_PUSH_6mm
U1, U2: DS18S20_; TO-92-3; MPN DS18S20+; Digi-Key_PN DS18S20+-ND
U3: TPIC6595; DIP-20_W7.62mm_LongPads

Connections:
+5V: J4.3
GND: C1.1, D5.1 (K), D6.1 (K), D7.1 (K), D13.1 (K), D14.1 (K), D20.2 (A), ENC1.C (COMMON), J1.4, J2.4, J3.4, J4.4, J5.4, J6.4, J7.4, J8.4, J9.4, J10.4, J16.4, R4.1, R8.1, R9.1, R10.1, R12.1, R20.2, RLY2.2 (COIL), RV1.3, RV2.3, U1.1 (GND), U2.1 (GND), U3.1 (PGND), U3.9 (~G), U3.10 (PGND), U3.11 (PGND), U3.19 (LGND), U3.20 (PGND)
unnamed: D1.1 (K), J1.2, R8.2
unnamed: D1.2 (A), R1.2
unnamed: D2.1 (K), J1.1, R12.2
unnamed: D2.2 (A), R2.1
unnamed: D3.1 (K), J2.2, R9.2
unnamed: D3.2 (A), R3.2
unnamed: D5.2 (A), R5.1
unnamed: D6.2 (A), R6.1
unnamed: D7.2 (A), R7.1
unnamed: D8.1 (K), J2.1, R10.2
unnamed: D8.2 (A), R11.1
unnamed: D9.1 (K), R13.1
unnamed: D10.1 (K), R14.1
unnamed: D11.1 (K), R15.1
unnamed: D12.1 (K), R16.1
unnamed: D13.2 (A), R27.2
unnamed: D14.2 (A), R21.2
unnamed: D15.1 (K), R22.1
unnamed: D16.1 (K), R23.1
unnamed: D17.1 (K), R24.1
unnamed: D18.1 (K), R25.1
unnamed: D20.1 (K), J9.2, RLY2.5 (COIL)
unnamed: D22.1 (K), R20.1
unnamed: D22.2 (A), RLY2.3 (NO)
unnamed: ENC1.A (CHANNEL_A), J10.1
unnamed: ENC1.B (CHANNEL_B), J10.2
unnamed: J3.1, Q1.1 (C)
unnamed: J3.2, Q1.2 (E), R4.2
unnamed: J3.3, R5.2
unnamed: J4.1, R6.2
unnamed: J4.2, R7.2
unnamed: J5.1, RV1.2
unnamed: J5.2, RV2.2
unnamed: J5.3, R17.2, R26.2
unnamed: J6.3, J11.1, J12.1
unnamed: J7.1, U3.8 (~SRCLR)
unnamed: J7.2, U3.3 (SER_IN)
unnamed: J8.1, U3.13 (SRCK)
unnamed: J8.2, U3.12 (RCLK)
unnamed: J9.3, RLY2.1 (COM)
unnamed: J16.2, R18.2, U1.2 (DQ), U2.2 (DQ)
unnamed: R1.1, SW1.2
unnamed: R2.2, SW2.2
unnamed: R3.1, SW3.2
unnamed: R11.2, SW4.2
unnamed: R13.2, U3.14 (DRAIN4)
unnamed: R14.2, U3.15 (DRAIN5)
unnamed: R15.2, U3.16 (DRAIN6)
unnamed: R16.2, U3.17 (DRAIN7)
unnamed: R17.1, RV1.1
unnamed: J12.2, R21.1
unnamed: R22.2, U3.7 (DRAIN3)
unnamed: R23.2, U3.6 (DRAIN2)
unnamed: R24.2, U3.5 (DRAIN1)
unnamed: R25.2, U3.4 (DRAIN0)
unnamed: R26.1, RV2.1
unnamed: J11.2, R27.1
button_5v: J1.3, J2.3, SW1.1, SW2.1, SW3.1, SW4.1
reg_5V: C1.2, D9.2 (A), D10.2 (A), D11.2 (A), D12.2 (A), D15.2 (A), D16.2 (A), D17.2 (A), D18.2 (A), J7.3, J8.3, U3.2 (VCC)
temp_5V: J16.3, R18.1, U1.3 (VDD), U2.3 (VDD)

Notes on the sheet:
digital output
analog input
Testing properties: - Digital output (PWM can be incorporated in the same one) - Digital input - Analog input - Shift register - H-bridge - Solenoid driver - Temperature sensor
IR sensor
Jumper demo
+5V
relays
digital input
temperature sensor

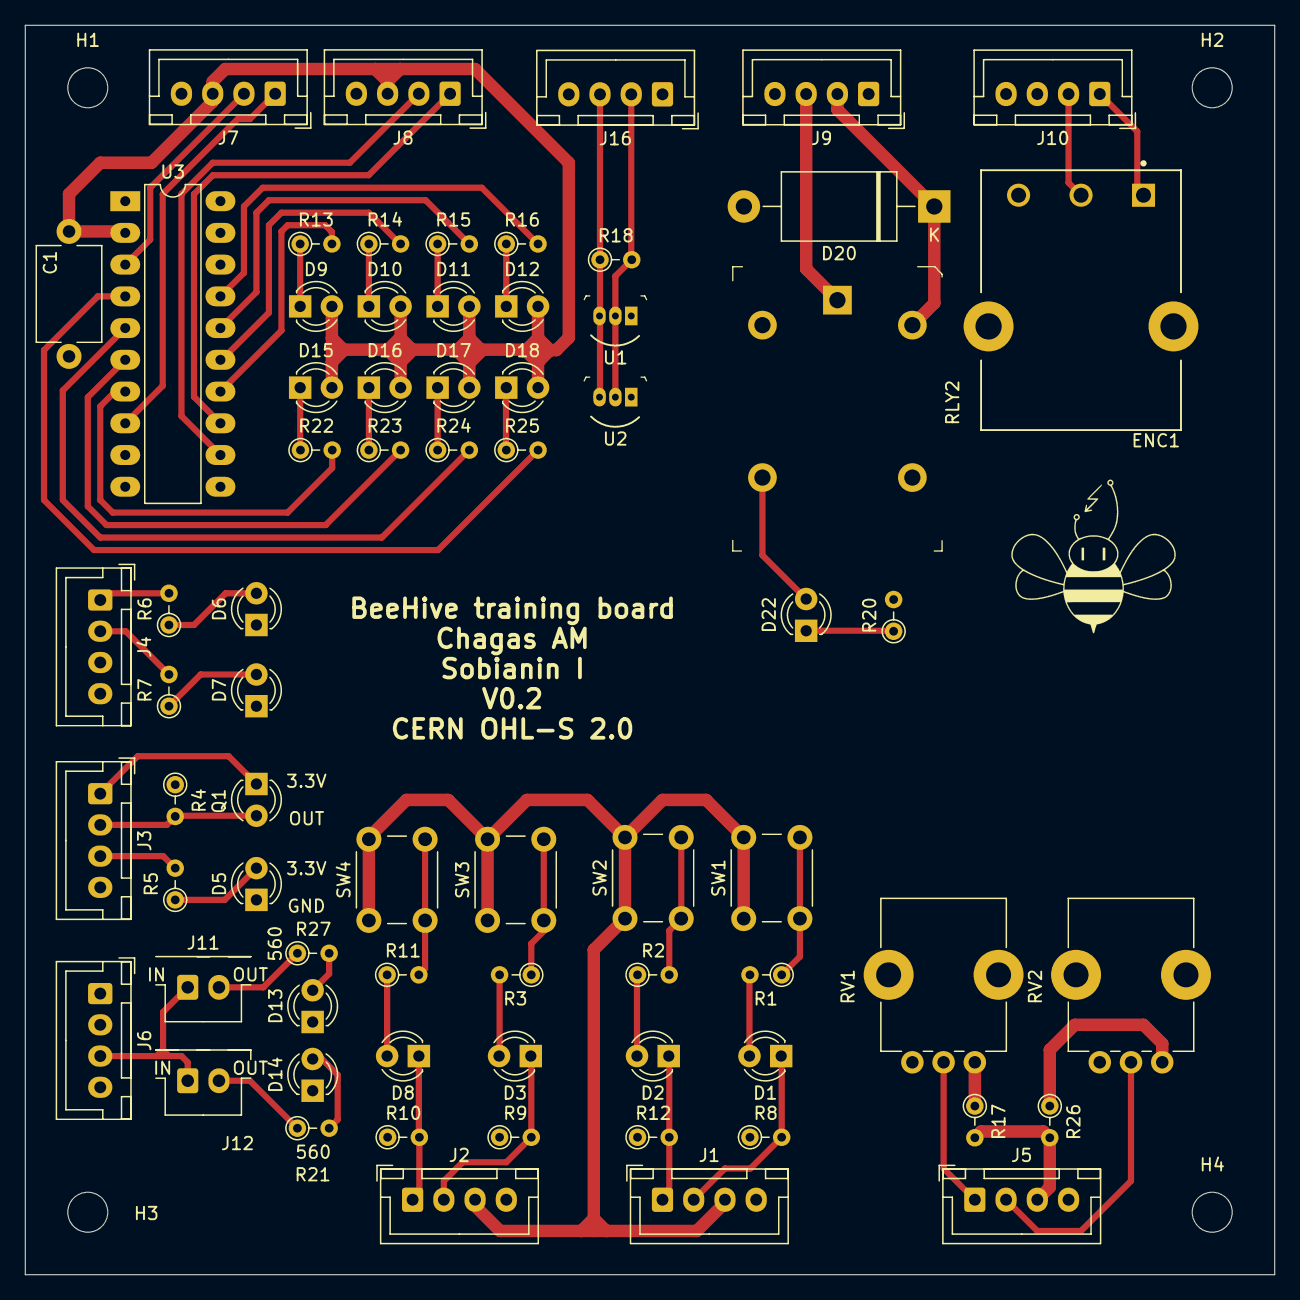
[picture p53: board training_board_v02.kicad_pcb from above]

Board: 2 copper layers, 100.0 x 100.0 mm, 75 parts (0 on the bottom side), 61 nets.

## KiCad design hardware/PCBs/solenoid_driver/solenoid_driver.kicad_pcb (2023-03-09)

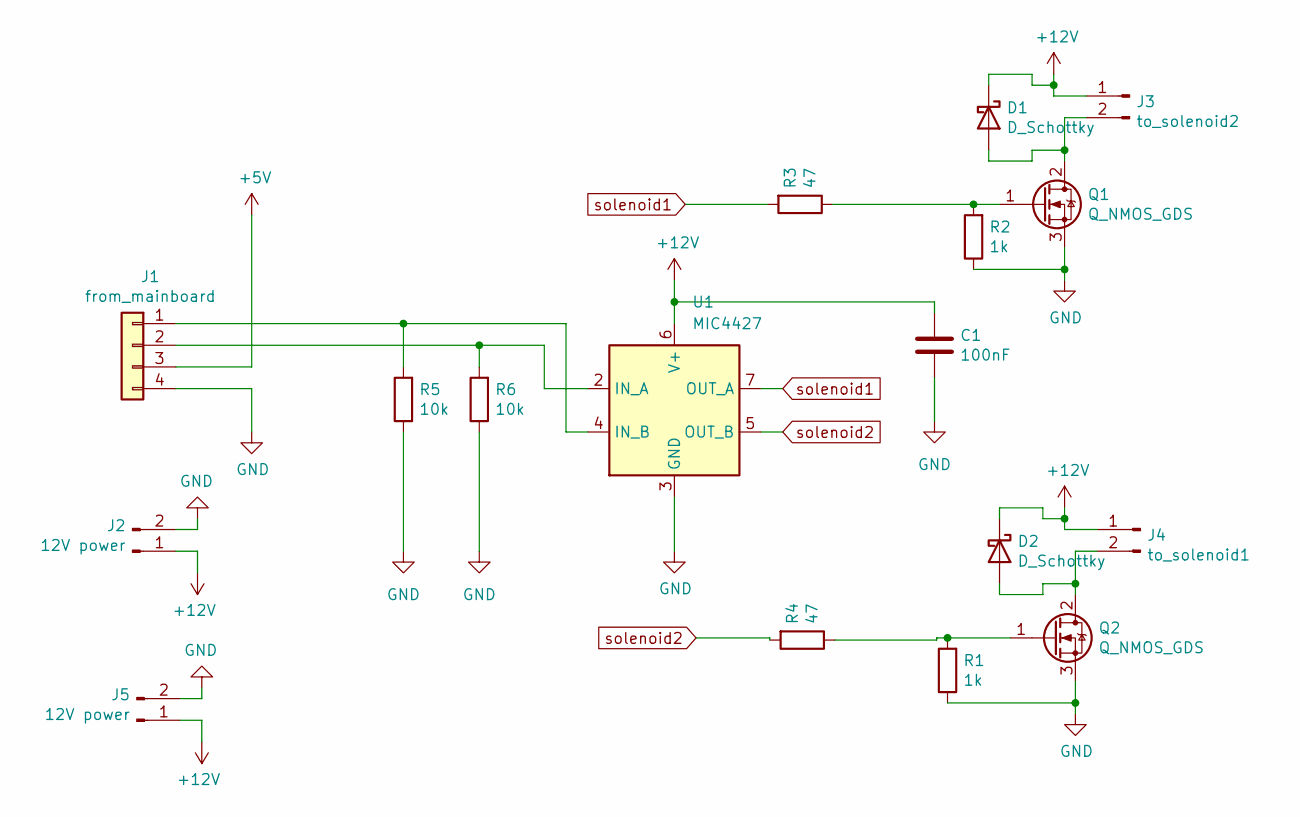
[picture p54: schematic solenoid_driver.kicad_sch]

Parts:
C1: 100nF; C_Disc_D7.0mm_W2.5mm_P5.00mm
D1, D2: D_Schottky; D_DO-201AD_P15.24mm_Horizontal
J1: from_mainboard; JST_XH_B4B-XH-A_1x04_P2.50mm_Vertical
J2, J5: 12V power; JST_XH_B2B-XH-A_1x02_P2.50mm_Vertical
J3: to_solenoid2; JST_XH_B2B-XH-A_1x02_P2.50mm_Vertical
J4: to_solenoid1; JST_XH_B2B-XH-A_1x02_P2.50mm_Vertical
Q1, Q2: Q_NMOS_GDS; TO-220-3_Vertical
R1, R2: 1k; R_Box_L13.0mm_W4.0mm_P9.00mm
R3, R4: 47; R_Box_L13.0mm_W4.0mm_P9.00mm
R5, R6: 10k; R_Box_L13.0mm_W4.0mm_P9.00mm
U1: MIC4427; DIP-8_W7.62mm

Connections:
+5V: J1.3
+12V: C1.1, D1.1 (K), D2.1 (K), J2.1, J3.1, J4.1, J5.1, U1.6 (V+)
GND: C1.2, J1.4, J2.2, J5.2, Q1.3 (S), Q2.3 (S), R1.1, R2.1, R5.1, R6.1, U1.3 (GND)
unnamed: D1.2 (A), J3.2, Q1.2 (D)
unnamed: D2.2 (A), J4.2, Q2.2 (D)
unnamed: J1.1, R5.2, U1.4 (IN_B)
unnamed: Q1.1 (G), R2.2, R3.1
unnamed: Q2.1 (G), R1.2, R4.1
unnamed: J1.2, R6.2, U1.2 (IN_A)
solenoid1: R3.2, U1.7 (OUT_A)
solenoid2: R4.2, U1.5 (OUT_B)

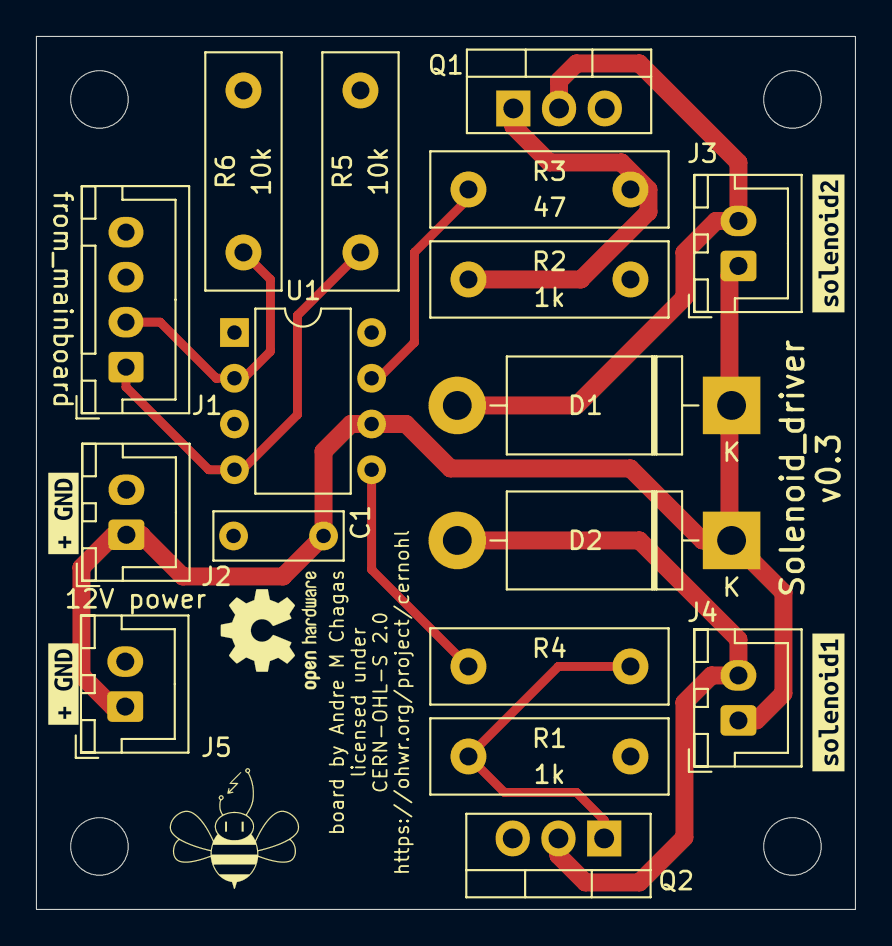
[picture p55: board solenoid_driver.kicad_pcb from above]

Board: 2 copper layers, 45.5 x 48.5 mm, 21 parts (0 on the bottom side), 10 nets.

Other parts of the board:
kibuzzard-63063C94: G***; kibuzzard-63063C94
kibuzzard-63064E8E: G***; kibuzzard-63064E8E
kibuzzard-63064EFA: G***; kibuzzard-63064EFA
kibuzzard-63065932: G***; kibuzzard-63065932

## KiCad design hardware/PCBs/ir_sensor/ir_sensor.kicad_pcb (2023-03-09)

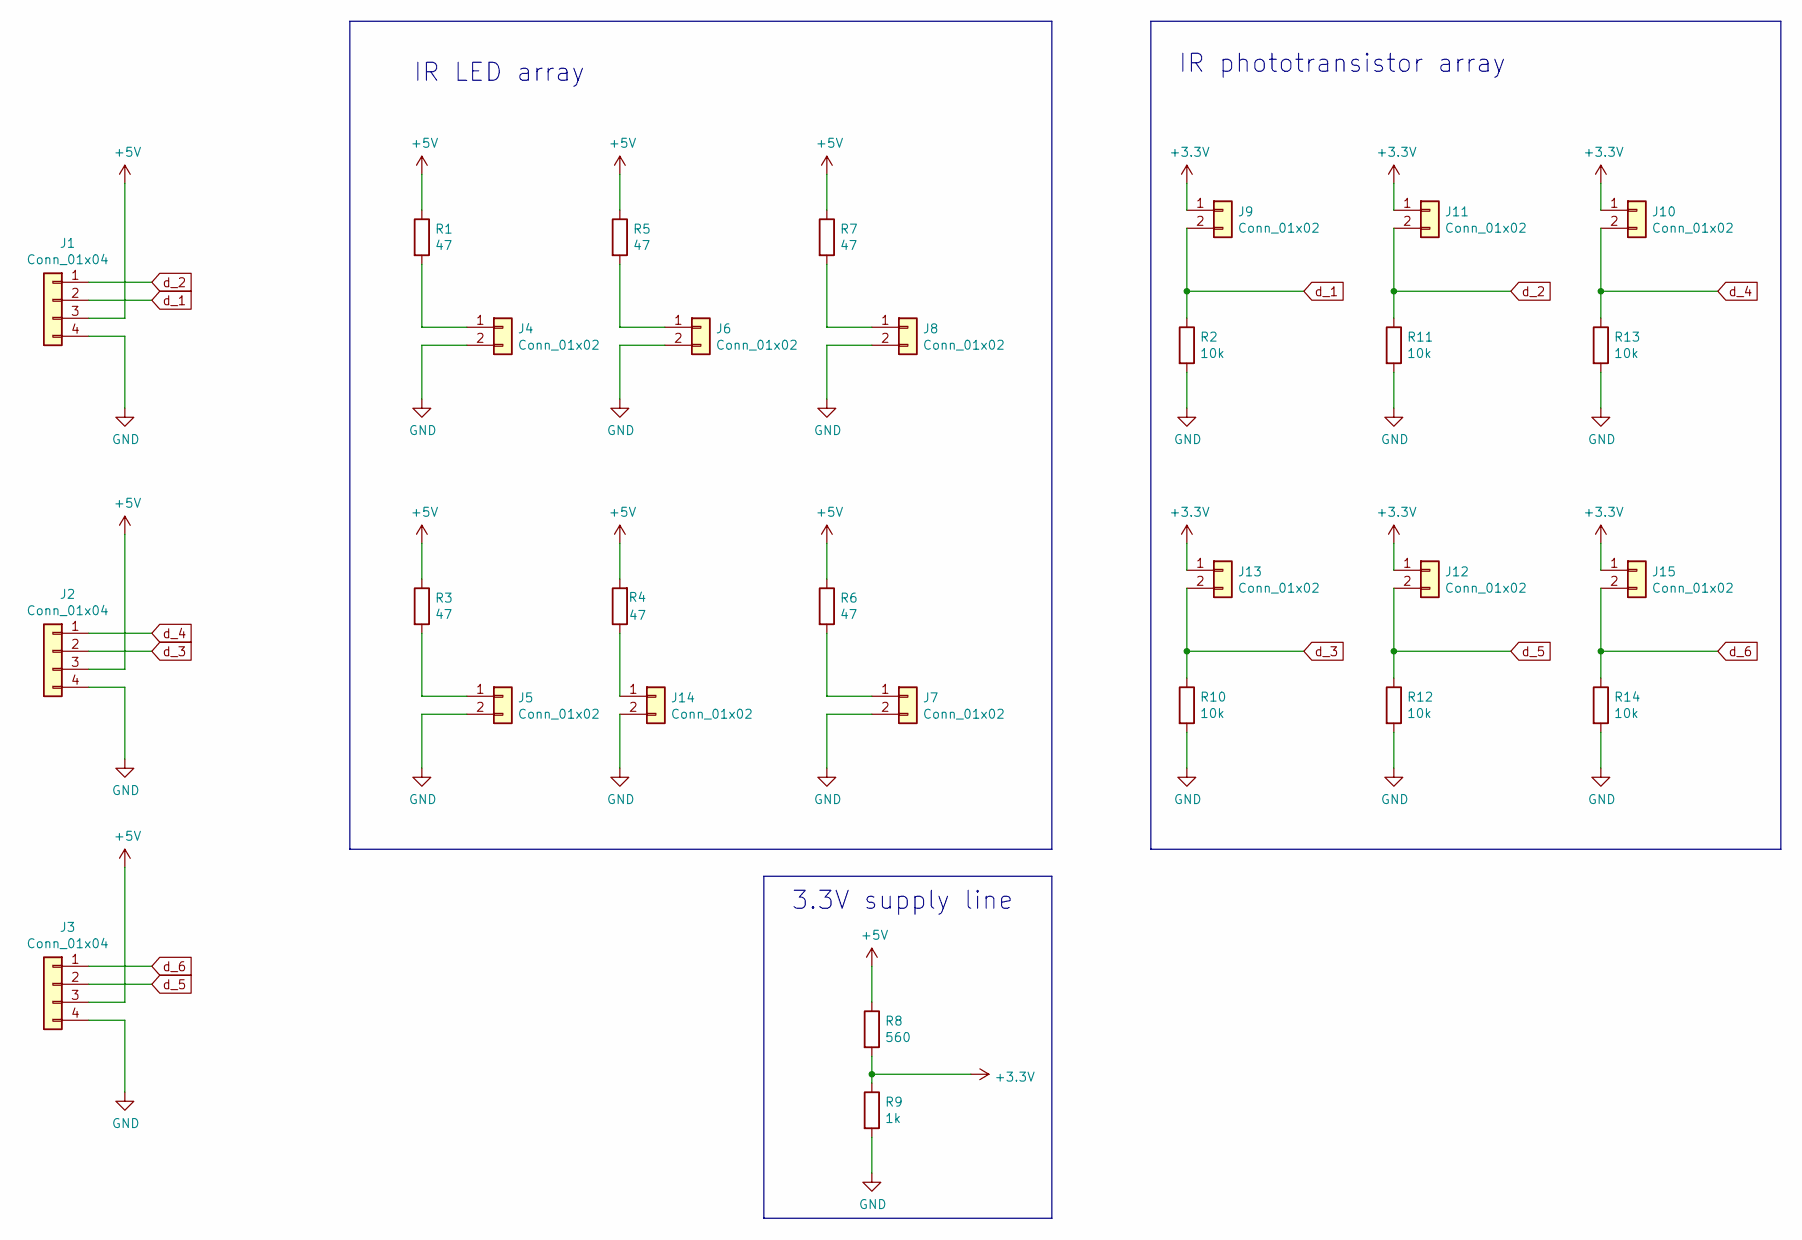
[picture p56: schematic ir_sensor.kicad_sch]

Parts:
J1, J2, J3: Conn_01x04; JST_XH_B4B-XH-A_1x04_P2.50mm_Vertical
J4, J5, J6, J7, J8, J9, J10, J11, J12, J13, J14, J15: Conn_01x02; JST_XH_B2B-XH-A_1x02_P2.50mm_Vertical
R1, R3, R4, R5, R6, R7: 47; R_Box_L13.0mm_W4.0mm_P9.00mm
R2, R10, R11, R12, R13, R14: 10k; R_Box_L13.0mm_W4.0mm_P9.00mm
R8: 560; R_Box_L13.0mm_W4.0mm_P9.00mm
R9: 1k; R_Box_L13.0mm_W4.0mm_P9.00mm

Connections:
+3V3: J9.1, J10.1, J11.1, J12.1, J13.1, J15.1, R8.2, R9.1
+5V: J1.3, J2.3, J3.3, R1.1, R3.1, R4.2, R5.1, R6.1, R7.1, R8.1
GND: J1.4, J2.4, J3.4, J4.2, J5.2, J6.2, J7.2, J8.2, J14.2, R2.2, R9.2, R10.2, R11.2, R12.2, R13.2, R14.2
unnamed: J4.1, R1.2
unnamed: J5.1, R3.2
unnamed: J6.1, R5.2
unnamed: J7.1, R6.2
unnamed: J8.1, R7.2
unnamed: J14.1, R4.1
d_1: J1.2, J9.2, R2.1
d_2: J1.1, J11.2, R11.1
d_3: J2.2, J13.2, R10.1
d_4: J2.1, J10.2, R13.1
d_5: J3.2, J12.2, R12.1
d_6: J3.1, J15.2, R14.1

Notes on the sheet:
3.3V supply line
IR LED array
IR phototransistor array

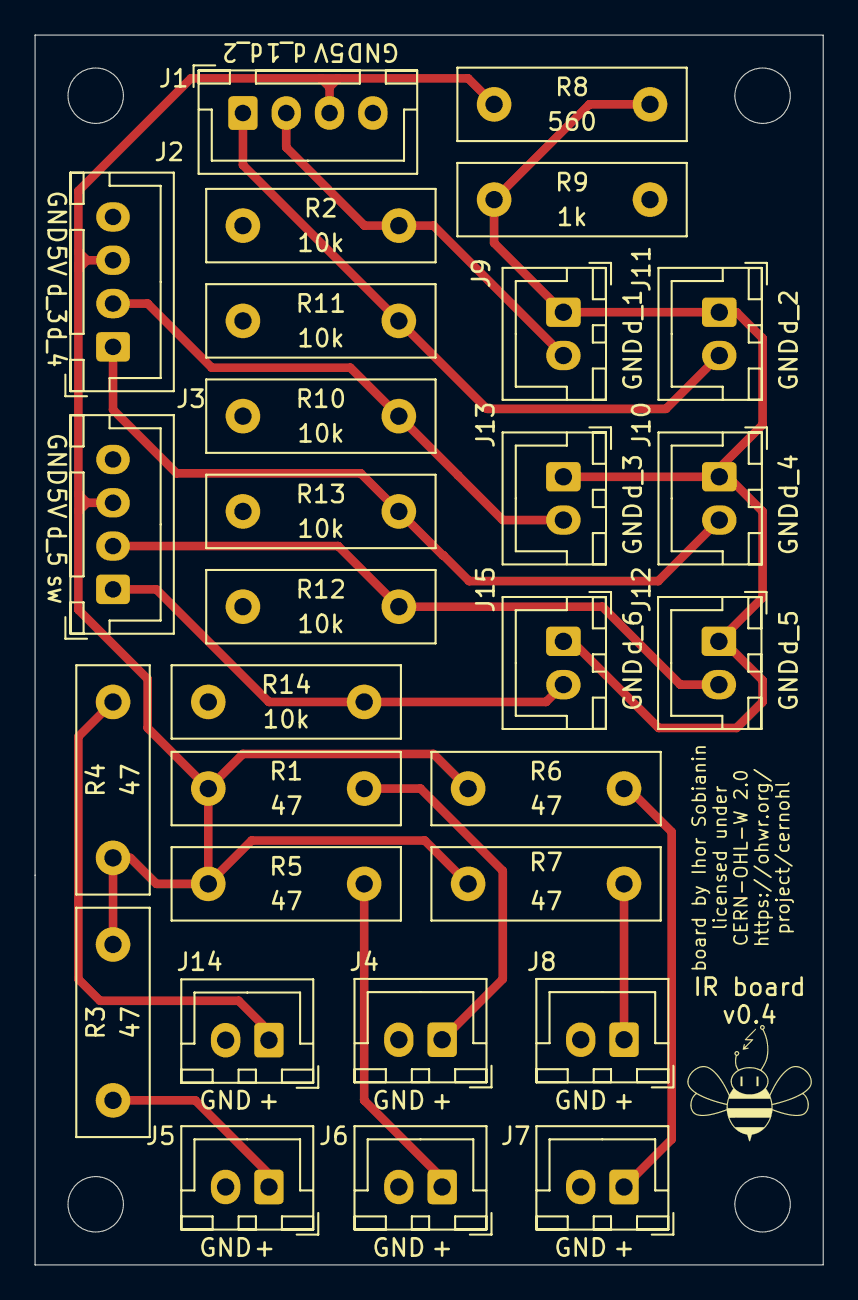
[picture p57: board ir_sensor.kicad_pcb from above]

Board: 2 copper layers, 45.5 x 71.0 mm, 29 parts (0 on the bottom side), 15 nets.

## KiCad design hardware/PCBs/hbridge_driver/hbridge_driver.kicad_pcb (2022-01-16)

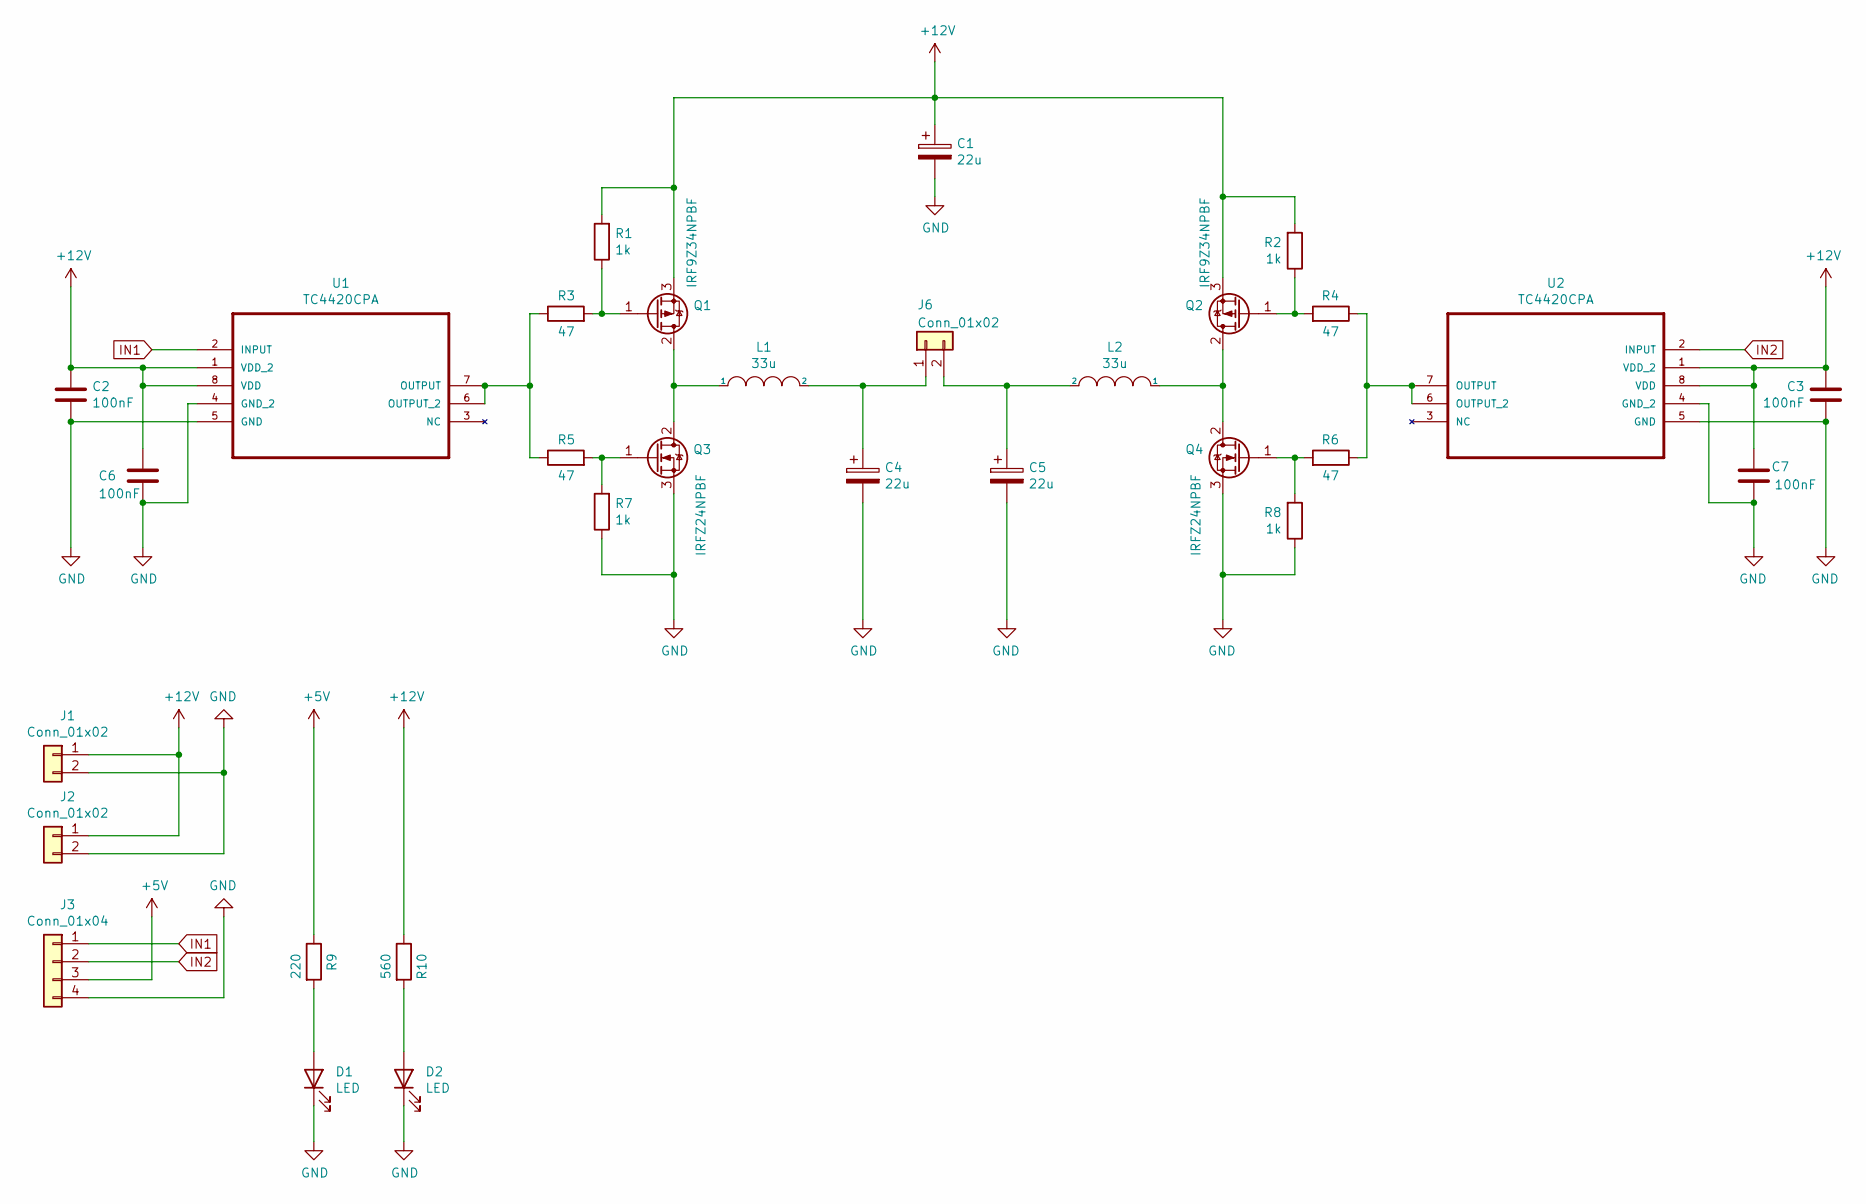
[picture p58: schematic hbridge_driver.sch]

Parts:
C1, C4, C5: 22u; CP_Radial_D5.0mm_P2.00mm
C2, C3, C6, C7: 100nF; C_Disc_D7.0mm_W2.5mm_P5.00mm
D1, D2: LED; LED_D3.0mm
J1, J2, J6: Conn_01x02; JST_XH_B2B-XH-A_1x02_P2.50mm_Vertical
J3: Conn_01x04; JST_XH_B4B-XH-A_1x04_P2.50mm_Vertical
L1, L2: 33u; L_Radial_D10.0mm_P5.00mm_Neosid_SD12_style3
Q1, Q2: IRF9Z34NPBF; TO-220-3_Vertical
Q3, Q4: IRFZ24NPBF; TO-220-3_Vertical
R1, R2, R7, R8: 1k; R_Box_L13.0mm_W4.0mm_P9.00mm
R3, R4, R5, R6: 47; R_Box_L13.0mm_W4.0mm_P9.00mm
R9: 220; R_Box_L13.0mm_W4.0mm_P9.00mm
R10: 560; R_Box_L13.0mm_W4.0mm_P9.00mm
U1, U2: TC4420CPA; DIP-8_W7.62mm

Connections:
+5V: J3.3, R9.1
+12V: C1.1, C2.1, C3.1, C6.1, C7.1, J1.1, J2.1, Q1.3 (S), Q2.3 (S), R1.2, R2.2, R10.1, U1.1 (VDD_2), U1.8 (VDD), U2.1 (VDD_2), U2.8 (VDD)
GND: C1.2, C2.2, C3.2, C4.2, C5.2, C6.2, C7.2, D1.1 (K), D2.1 (K), J1.2, J2.2, J3.4, Q3.3 (S), Q4.3 (S), R7.1, R8.1, U1.4 (GND_2), U1.5 (GND), U2.4 (GND_2), U2.5 (GND)
IN1: J3.1, U1.2 (INPUT)
IN2: J3.2, U2.2 (INPUT)
unnamed: C4.1, J6.1, L1.2
unnamed: C5.1, J6.2, L2.2
unnamed: D1.2 (A), R9.2
unnamed: D2.2 (A), R10.2
unnamed: L1.1, Q1.2 (D), Q3.2 (D)
unnamed: L2.1, Q2.2 (D), Q4.2 (D)
unnamed: Q1.1 (G), R1.1, R3.2
unnamed: Q2.1 (G), R2.1, R4.2
unnamed: Q3.1 (G), R5.2, R7.2
unnamed: Q4.1 (G), R6.2, R8.2
unnamed: R3.1, R5.1, U1.6 (OUTPUT_2), U1.7 (OUTPUT)
unnamed: R4.1, R6.1, U2.6 (OUTPUT_2), U2.7 (OUTPUT)

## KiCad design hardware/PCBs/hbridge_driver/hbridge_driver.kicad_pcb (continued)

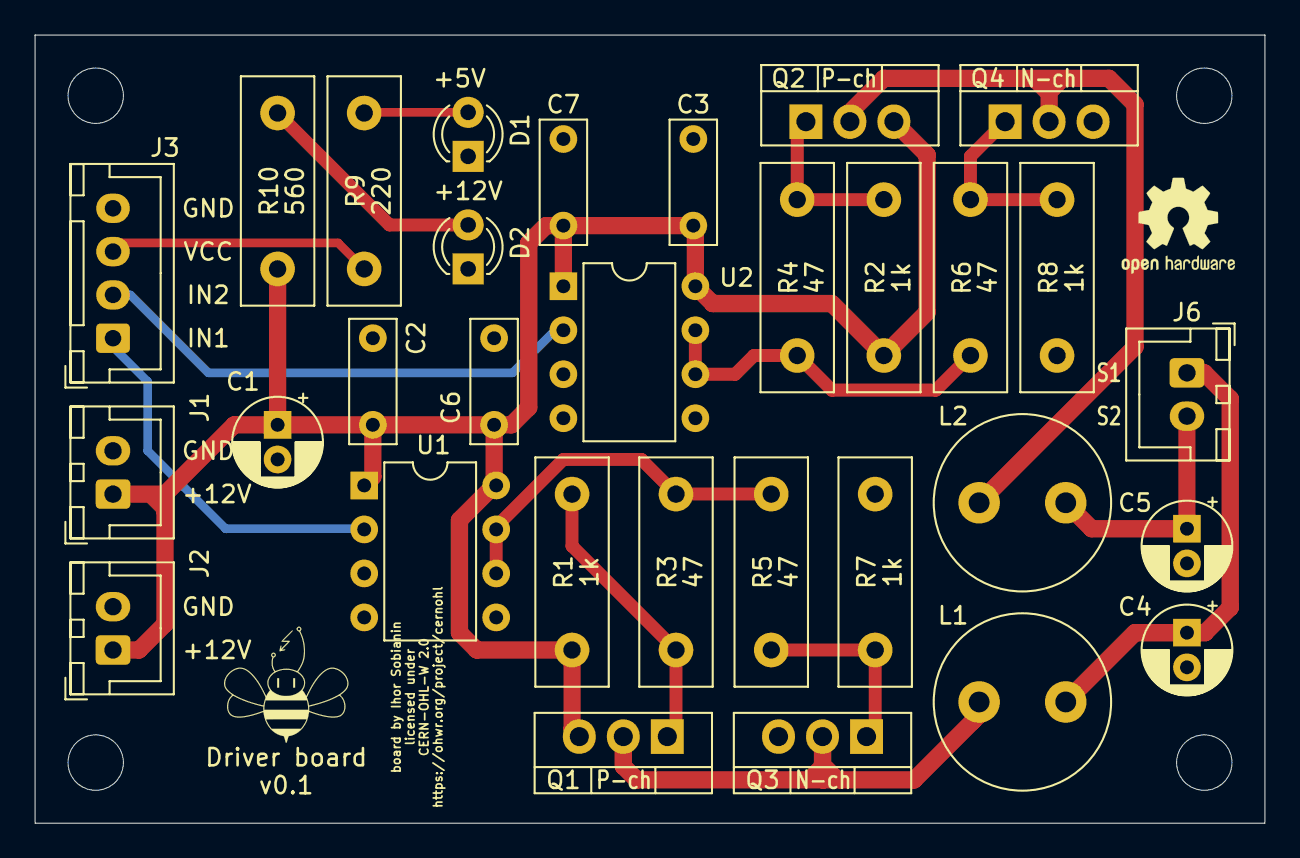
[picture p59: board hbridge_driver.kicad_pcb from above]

Board: 2 copper layers, 71.0 x 45.5 mm, 31 parts (0 on the bottom side), 17 nets.

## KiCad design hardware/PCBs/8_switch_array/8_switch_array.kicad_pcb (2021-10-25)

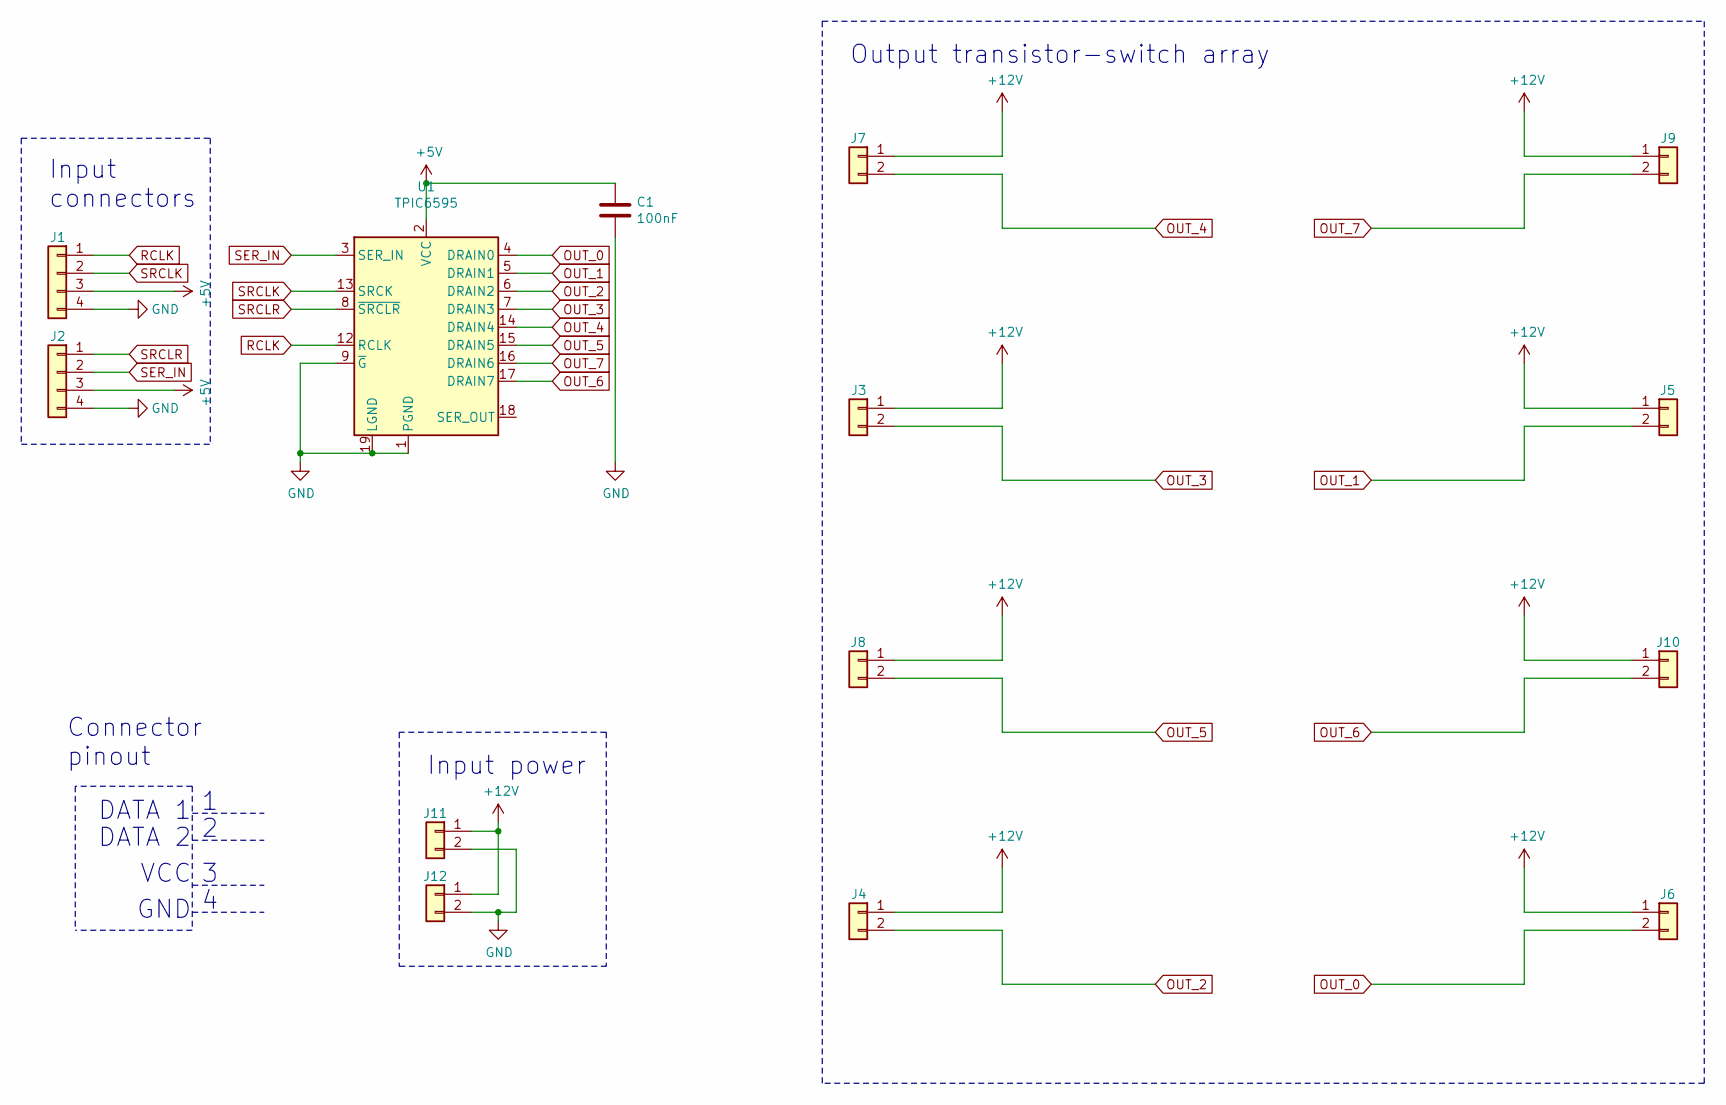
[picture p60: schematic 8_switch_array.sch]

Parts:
C1: 100nF; C_Disc_D7.0mm_W2.5mm_P5.00mm
J1, J2: Conn_01x04; JST_XH_B4B-XH-A_1x04_P2.50mm_Vertical
J3, J4, J5, J6, J7, J8, J9, J10, J11, J12: Conn_01x02; JST_XH_B2B-XH-A_1x02_P2.50mm_Vertical
U1: TPIC6595; DIP-20_W7.62mm

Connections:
+5V: C1.1, J1.3, J2.3, U1.2 (VCC)
+12V: J3.1, J4.1, J5.1, J6.1, J7.1, J8.1, J9.1, J10.1, J11.1, J12.1
GND: C1.2, J1.4, J2.4, J11.2, J12.2, U1.1 (PGND), U1.9 (~G), U1.10 (PGND), U1.11 (PGND), U1.19 (LGND), U1.20 (PGND)
OUT_0: J6.2, U1.4 (DRAIN0)
OUT_1: J5.2, U1.5 (DRAIN1)
OUT_2: J4.2, U1.6 (DRAIN2)
OUT_3: J3.2, U1.7 (DRAIN3)
OUT_4: J7.2, U1.14 (DRAIN4)
OUT_5: J8.2, U1.15 (DRAIN5)
OUT_6: J10.2, U1.17 (DRAIN7)
OUT_7: J9.2, U1.16 (DRAIN6)
RCLK: J1.1, U1.12 (RCLK)
SER_IN: J2.2, U1.3 (SER_IN)
SRCLK: J1.2, U1.13 (SRCK)
SRCLR: J2.1, U1.8 (~SRCLR)

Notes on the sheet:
Input power
Input connectors
Output transistor-switch array
GND
VCC
DATA 2
DATA 1
Connector pinout

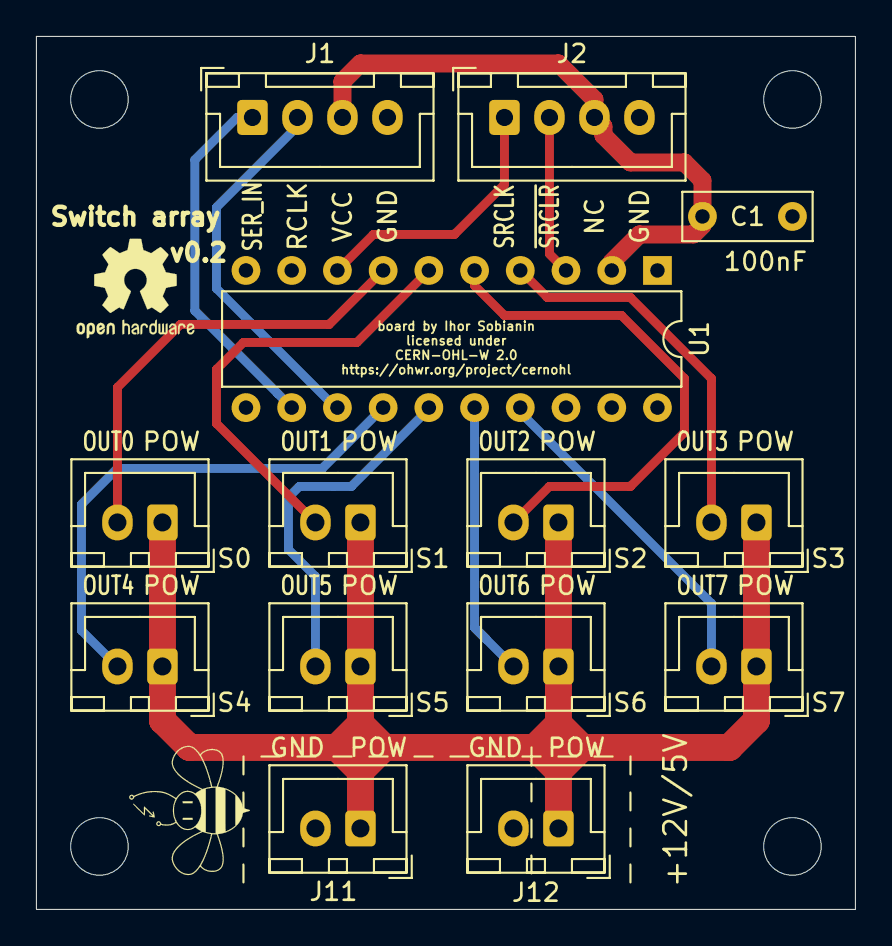
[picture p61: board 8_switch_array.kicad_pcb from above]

Board: 2 copper layers, 45.5 x 48.5 mm, 14 parts (0 on the bottom side), 15 nets.

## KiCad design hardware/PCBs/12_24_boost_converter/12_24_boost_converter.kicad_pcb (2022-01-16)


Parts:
C1, C2: 100nF; C_Disc_D5.1mm_W3.2mm_P5.00mm
C3: 22µF; CP_Radial_D5.0mm_P2.00mm
D1: 1N5822; D_DO-201AD_P15.24mm_Horizontal
D2: LED; LED_D3.0mm
J1, J2, J3, J4: Conn_01x02; JST_XH_B2B-XH-A_1x02_P2.50mm_Vertical
L1: 33µH; L_Radial_D10.0mm_P5.00mm_Neosid_SD12_style3
Q1: IRFZ24NPBF; TO-220-3_Vertical
R1, R2, R3: 47; R_Axial_DIN0411_L9.9mm_D3.6mm_P12.70mm_Horizontal
R4: 1k; R_Axial_DIN0411_L9.9mm_D3.6mm_P12.70mm_Horizontal
R5: 560; R_Axial_DIN0411_L9.9mm_D3.6mm_P12.70mm_Horizontal
U1: LM555xM; DIP-8_W7.62mm_LongPads

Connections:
+12V: J1.1, J2.1, L1.1, R1.1, R5.2, U1.4 (R), U1.8 (VCC)
+24V: C3.1, D1.1 (K), J3.1, J4.1
GND: C1.1, C2.1, C3.2, D2.1 (K), J1.2, J2.2, J3.2, J4.2, Q1.3 (S), R4.2, U1.1 (GND)
unnamed: C1.2, R2.1, U1.2 (TR), U1.6 (THR)
unnamed: C2.2, U1.5 (CV)
unnamed: D1.2 (A), L1.2, Q1.2 (D)
unnamed: D2.2 (A), R5.1
unnamed: Q1.1 (G), R3.1, R4.1
unnamed: R1.2, R2.2, U1.7 (DIS)
unnamed: R3.2, U1.3 (Q)

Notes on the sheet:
LM555's pin 3 frequency depends on pin 7 and 6 resistors values and pin 2 capacitor value, provided pin 5 capacitor remains constant. This configuration provides about 100kHz frequency. It can also be achieved with another set of components. The choice of components depends solely on what is more c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
***


Board: 2 copper layers, 45.5 x 48.5 mm, 17 parts (0 on the bottom side), 10 nets.

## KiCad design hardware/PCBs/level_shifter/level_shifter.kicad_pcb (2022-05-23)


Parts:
J1, J2: Conn_01x04; JST_XH_B4B-XH-A_1x04_P2.50mm_Vertical
J3, J4, J5, J6: Conn_01x02; JST_XH_B2B-XH-A_1x02_P2.50mm_Vertical
Q1, Q2, Q3, Q4: 2N7000; TO-92_Inline_Wide
R1: 560; R_Axial_DIN0411_L9.9mm_D3.6mm_P12.70mm_Horizontal
R2, R3, R4, R5, R6, R7, R8, R9, R10: 1k; R_Axial_DIN0411_L9.9mm_D3.6mm_P12.70mm_Horizontal

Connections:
+3V3: Q1.2 (G), Q2.2 (G), Q3.2 (G), Q4.2 (G), R1.1, R2.2, R3.1, R4.1, R5.1, R6.1
+5V: J1.3, J2.3, R1.2, R7.1, R8.1, R9.1, R10.1
GND: J1.4, J2.4, J3.2, J4.2, J5.2, J6.2, R2.1
d1_h: J3.1, Q1.3 (D), R7.2
d1_l: J1.2, Q1.1 (S), R3.2
d2_h: J4.1, Q2.3 (D), R8.2
d2_l: J1.1, Q2.1 (S), R4.2
d3_h: J5.1, Q3.3 (D), R9.2
d3_l: J2.2, Q3.1 (S), R5.2
d4_h: J6.1, Q4.3 (D), R10.2
d4_l: J2.1, Q4.1 (S), R6.2

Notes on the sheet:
3.25 V


Board: 2 copper layers, 45.5 x 48.5 mm, 20 parts (0 on the bottom side), 11 nets.

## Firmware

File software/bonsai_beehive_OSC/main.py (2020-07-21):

from machine import Pin
import network

# import uosc
import machine
from uosc.client import Bundle, Client, create_message
import time
import passes
import uarray


def main():
    # set timing variables:
    timePeriod = 20  # time in milliseconds between each data sending
    startTiming = 0
    stopTiming = 0

    # set variables for uosc client
    microsDelay = 20 * 1000  #  time delay in microseconds
    bonsaiAddress = "192.168.137.255"
    commPort = 9001
    digitalSend = "/digitalInput"
    digitalReceive = "/digitalOutput"

    # create osc client object
    osc = Client(bonsaiAddress, commPort)
    # set Digital pins

    # Digital output
    p0 = Pin(32, Pin.OUT)  # currently beehive D0 is IO32
    p1 = Pin(33, Pin.OUT)  # currently beehive D1 is IO33
    p2 = Pin(25, Pin.OUT)  # currently beehive D2 is IO25
    p3 = Pin(26, Pin.OUT)  # currently beehive D3 is IO26

    # index of pins set as output
    pinOutList = [p0, p1, p2, p3]
    pinOutIndex = [0, 1, 2, 3]
    # pinOutNum = [0,1,2,3]

    # digital input
    # p4 = Pin(27, Pin.IN) # currently beehive D4 is IO27
    p5 = Pin(14, Pin.IN)  # currently beehive D5 is IO14
    # p6 = Pin(12, Pin.IN) # currently beehive D6 is IO12
    # p7 = Pin(13, Pin.IN) # currently beehive D7 is IO13

    # index of pins set as input
    pinInList = [p5]  # [p4,p5,p6,p7]
    pinInIndex = [5]  # [4,5,6,7]

    # Analog input

    # although attenuation allows 3.6V to be the max range, 3.3V should be the MAX send to the board!!!
    # adc0 = machine.ADC(34) # currently beehive D7 is IO13
    # adc0.atten(machine.ADC.ATTN_11DB)    # set 11dB input attenuation (voltage range roughly 0.0v - 3.6v)
    # adc1 = machine.ADC(34) # currently beehive D7 is IO13
    # adc1.atten(machine.ADC.ATTN_11DB)    # set 11dB input attenuation (voltage range roughly 0.0v - 3.6v)
    # adc2 = machine.ADC(34) # currently beehive D7 is IO13
    # adc2.atten(machine.ADC.ATTN_11DB)    # set 11dB input attenuation (voltage range roughly 0.0v - 3.6v)
    # adc3 = machine.ADC(34) # currently beehive D7 is IO13
    # adc3.atten(machine.ADC.ATTN_11DB)    # set 11dB input attenuation (voltage range roughly 0.0v - 3.6v)

    # index of pins set as analog
    # pinsAnalogInList = [adc0,adc1,adc2,adc3]

    # analog output (actually PWM):
    # dac0 = 1
    # dac1 = 2
    # dac2 = 3
    # dac4 = 4

    # create bundle
    b = Bundle()
    # infinite loop

    while 1:

        # receive message from OSC
        dummie = 0
        # if there is a specific message break the scanning loop
        if dummie != 0:
            break

        # temp variable to store digital input values
        temp = 0

        startTiming = time.ticks_us()  # get microsecond counter
        # loop to scan input pins

        # tic1 = time.ticks_us()
        for i in range(len(pinInList)):
            # print(i)
            # print(pinInList[i].value())
            if pinInList[i].value() == 1:
                temp = temp + (2 ** pinInIndex[i])
            # print(temp)
        # toc1 = time.ticks_us()
        # print("getting all dig in ports took: "+str(toc1-tic1)+ " microseconds" )
        # print(toc1-tic1)
        # temp = bytes(temp)
        temp = uarray.array("B", [10, 32, 10, 20, 10, 10])
        msg = create_message(digitalSend, ("b", temp))
        b.add(msg)
        tic2 = time.ticks_us()
        osc.send(b)
        osc.close()
        del temp
        toc2 = time.ticks_us()
        print("sending took: " + str(toc2 - tic2) + " microseconds")
        x = 0
        while (
            stopTiming - startTiming < timePeriod * 1000
        ):  # convert milliseconds in microseconds
            # read digital port
            stopTiming = time.ticks_us()
        # time.sleep(0.001)

    # analog input pins
    # for i in range(len(pinsAnalogInList)):
    #    print(i)
    #    print(pinsAnalogInList[i].adc.read_u16())
    # do not forget to actually send the adc read info.

    # send message out with pins state

    # listen for message setting pins
    return


# automatically start main

# if __name__ == '__main__':
#    print("main entered")
#    #esp.osdebug(0)
#    main()


def reset():
    machine.reset()
    return

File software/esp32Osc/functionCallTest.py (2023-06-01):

# Example 1 - using String?
# eval("Pin(13,Pin.OUT).value(0)")

# Example 2
# /function_name argv argc
# call function_name(argv,argc)

# Example 3
# Send the return value back to bonsai as a OSC message.

# Example 4
# Reactive Callback
# ex: Sample all analog countinuasly while receiving messages.

# Example 5
# use OSC timestamps in previous examples.

import network

try:
    import socket
except ImportError:
    import usocket as socket

try:
    import logging
except ImportError:
    import uosc.fakelogging as logging

    
from uosc.server import handle_osc
from machine import Pin
from uosc.client import Bundle, Client, create_message
import passes
    
log = logging.getLogger("uosc.minimal_server")
#DEFAULT_ADDRESS = '10.20.23.46'
#DEFAULT_ADDRESS = '192.168.1.141'
DEFAULT_ADDRESS = network.WLAN().ifconfig()[0]
DEFAULT_PORT = 9001
MAX_DGRAM_SIZE = 1472
osc = Client(passes.OscComputerAddress, passes.commPort)


def coustumFunction(pinNumber,pinMode,value):
    mypin = Pin(pinNumber,pinMode)
    mypin.value(value)
    return

def definePin(pinNumber,pinMode):
    mypin = Pin(pinNumber,pinMode)
    return mypin

def digitalWrite(mypin, value):
    mypin.value(value)
    return

def digitalRead(mypin):
    return mypin.value()

def digitalRead2(pinNumber):
    mypin = Pin(pinNumber)
    return mypin.value()

def analogRead(mypin):
    #check if there is a way to check if an assigned pin is capable of analog read
    pass

def analogWrite(mypin):
    #check if there is a way to check if an assigned pin is capable of analog write
    pass

# def pwm write

def dispatch (timetag, message):
    #Pin(13,Pin.OUT).value(0)
    print(timetag)
    print(message)
    if (message[0] == '/eval'):
        eval(message[2][0])
    #  send back return value of eval
    elif (message[0] == '/definePin'):
        test = definePin(message[2][0],eval(message[2][1]))
        print(test)
        osc.send('/definePin/return', repr(test))
    elif (message[0] == '/digitalRead'):
        test = digitalRead(eval(message[2][0]))
        print(test)
        osc.send('/digitalRead/return', test)
    elif (message[0] == '/digitalRead2'):
        test = digitalRead2(message[2][0])
        print(test)
        osc.send('/digitalRead2/return', test)
    elif (message[0] == '/coustumFunction'):
        coustumFunction(message[2][0],eval(message[2][1]), message[2][2])
    # send back return value of mycoustum funtion.
    else:
        print(message[0][1:])
        #eval(message[0][1:]+str(message[2]))
    return

def run_server(saddr = DEFAULT_ADDRESS, port = DEFAULT_PORT, handler=handle_osc):
    sock = socket.socket(socket.AF_INET, socket.SOCK_DGRAM)
    sock.setsockopt(socket.SOL_SOCKET, socket.SO_REUSEADDR, 1)
    ai = socket.getaddrinfo(saddr, port)[0]
    sock.bind(ai[-1])
    log.info("Listening for OSC messages on %s:%i.", saddr, port)
    
    #osc = Client(passes.OscComputerAddress, passes.commPort)
    osc.send('/Server', "Start")
    # osc.send('/Interface/coustumFunction',,,) # send interface to bonsai
    # osc.send('/Server/Address',saddr,port) #see if this is usefull or redundant

    try:
        while True:
            data, caddr = sock.recvfrom(MAX_DGRAM_SIZE)
            if __debug__: log.debug("RECV %i bytes from %s:",
                                    len(data),data)
#            if __debug__: log.debug("RECV %i bytes from %s:%s",
#                                    len(data), *get_hostport(caddr))
            handler(data,caddr,dispatch)
    finally:
        sock.close()
        log.info("Bye!")

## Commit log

2020-01-16 PCB file and cache library for schematics
    [flypi_v2.kicad_pcb]
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2020-01-16 Schematics for the hub
    [flypi_v2.sch]
2020-01-17 Gerber files for manufacturing
    [flypi_v2-B_Cu.gbr, flypi_v2-F_CrtYd.gbr, flypi_v2-F_Cu.gbr, flypi_v2-F_Fab.gbr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]
2020-01-17 Update flypi_v2.kicad_pcb
    Added new dimensions to the PCB
    [flypi_v2.kicad_pcb]
2020-01-17 Now Kitspace shows PCB correctly
    I could not figure out why the PCB was yellow. All zones were filled with yellow and the silk text was not visible. Looked horrible. However, other viewers worked correctly (used oshpark.com viewer).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
    [flypi_v2-B_Adhes.gbr, flypi_v2-B_Cu.gbr, flypi_v2-B_Fab.gbr, flypi_v2-B_Mask.gbr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]
2020-01-23 Added more information regarding connector pinout
    [flypi_v2.sch]
2020-01-25 Changed pinout to VCC-GND
    [4_switch_array-B_Adhes.gbr, 4_switch_array-B_CrtYd.gbr, 4_switch_array-B_Cu.gbr, 4_switch_array-B_Fab.gbr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]
2020-01-25 Updated topology near C4 L2
    [flypi_v2-B_Adhes.gbr, flypi_v2-B_CrtYd.gbr, flypi_v2-B_Cu.gbr, flypi_v2-B_Fab.gbr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]
2020-06-11 more software testing, and adding libraries
    [1-click-bom.csv]
2020-06-11 organize folders
    [1-click-bom.csv, 4_switch_array-B_Adhes.gbr, 4_switch_array-B_CrtYd.gbr, 4_switch_array-B_Cu.gbr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]
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2020-06-29 Redesigned version of the main hub
    [1-click-bom.csv, 1-click-bom.tsv, beehive-B_Adhes.gbr, beehive-B_CrtYd.gbr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]
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2020-08-21 update power supply
    [power_supply-B_Adhes.gbr, power_supply-B_CrtYd.gbr, power_supply-B_Cu.gbr, power_supply-B_Fab.gbr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]
2020-08-21 move older board versions to archive folder
    [1-click-bom.csv, 4_switch_array-B_Adhes.gbr, 4_switch_array-B_CrtYd.gbr, 4_switch_array-B_Cu.gbr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]
2020-08-21 update main hub
    [beehive-B_Adhes.gbr, beehive-B_CrtYd.gbr, beehive-B_Cu.gbr, beehive-B_Fab.gbr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]
2020-08-21 update temp/humid sensor
    [hum_temp_sensor-B_Adhes.gbr, hum_temp_sensor-B_CrtYd.gbr, hum_temp_sensor-B_Cu.gbr, hum_temp_sensor-B_Fab.gbr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]
2020-08-21 update gas sensor
    [gas_sensor-B_Adhes.gbr, gas_sensor-B_CrtYd.gbr, gas_sensor-B_Cu.gbr, gas_sensor-B_Fab.gbr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]
2020-08-21 update v3 4 switch array
    [4_switch_array-B_Adhes.gbr, 4_switch_array-B_CrtYd.gbr, 4_switch_array-B_Cu.gbr, 4_switch_array-B_Fab.gbr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]
2020-08-21 update 8 switch array
    [8_switch_array-B_Adhes.gbr, 8_switch_array-B_CrtYd.gbr, 8_switch_array-B_Cu.gbr, 8_switch_array-B_Fab.gbr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]
2020-08-21 update central hub silk --> channel names
    [beehive-B_Adhes.gbr, beehive-B_CrtYd.gbr, beehive-B_Cu.gbr, beehive-B_Fab.gbr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]
2020-09-28 update 1-click boms
    [1-click-bom.csv]
2020-10-16 Update PCB files
    [12V5A_breakout-B_Adhes.gbr, 12V5A_breakout-B_CrtYd.gbr, 12V5A_breakout-B_Cu.gbr, 12V5A_breakout-B_Fab.gbr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]
2020-10-17 Update temp and gas sensors
    Minor changes: added screenshots of temp/humidity sensor, changed gas sensor pin names on PCB
    [gas_sensor-F_Cu.gbr, gas_sensor-F_SilkS.gbr, gas_sensor.kicad_pcb, hum_temp_sensor.kicad_pcb]
2020-10-17 Update silk layer
    [hum_temp_sensor-F_Cu.gbr, hum_temp_sensor-F_SilkS.gbr, hum_temp_sensor.kicad_pcb]
2020-10-18 Add custom libraries
    Add custom schematic symbols, footprints and 3D models
    [gas_sensor.kicad_pcb]
2020-10-18 Quick pinout fix for Peltier driver
    Simple fix with pinout now being correct
    [peltier-B_Adhes.gbr, peltier-B_CrtYd.gbr, peltier-B_Cu.gbr, peltier-B_Fab.gbr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]
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2020-12-11 Update on 12V5A system power line
    - 12V5A power line is now represented by two connectors with 2 pins across all the modules
    - all .png previews are updated. The central hub now has previews for schematics, PCB tracing and 3D model
    - peltier module now has two 12V5A connectors with redesigned one side of the bridge. Now all MOSFETs can be equipped with heatsinks
    - hum/temp sensor now has its connector position reversed to mimic Grove's one
    - hum/temp and gas sensors now have a small BeeHive logo on front layer rather than one big on back layer
    - hum/temp sensor now use only one layer for signals and one layer for ground
    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
    [4_switch_array-B_Adhes.gbr, 4_switch_array-B_CrtYd.gbr, 4_switch_array-B_Cu.gbr, 4_switch_array-B_Fab.gbr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]
2020-12-17 Add high power LED switch draft
    A rough draft of what is coming. The schematics includes MOSFETS with drivers and all complementary components
    [hp_led_switch.kicad_pcb, hp_led_switch.sch]
2020-12-19 Add high power switch and change 4 switch array
    - added high power switch
    - removed shift register from 4 switch array
    - changed some references on silk layer
    - small changes in switch arrays' tracing (width and paths)
    [1-click-bom.csv, 4_switch_array-B_Adhes.gbr, 4_switch_array-B_CrtYd.gbr, 4_switch_array-B_Cu.gbr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]
2021-02-14 Update 5V3A breakout
    - added LED for 12V5A line;
    - added two 5V3A line connectors added;
    - implemented board version as text marking on PCB;
    - changed the size of PCB to match others;
    [power_supply-B_Adhes.gbr, power_supply-B_CrtYd.gbr, power_supply-B_Cu.gbr, power_supply-B_Fab.gbr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]
2021-02-20 Add version number to boards
    Add version number to boards and update screenshots, zip gerber archives
    [12V5A_breakout-F_SilkS.gbr, 12V5A_breakout.kicad_pcb, 4_switch_array-F_SilkS.gbr, 4_switch_array.kicad_pcb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]
2021-04-14 add yaml file to add boards to kitspace. starting with four boards for testing
    [1-click-bom.csv, 4_switch_array-B_Adhes.gbr, 4_switch_array-B_CrtYd.gbr, 4_switch_array-B_Cu.gbr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]
2021-04-14 add items to ho led board 1-click-bom.csv file
    [1-click-bom.csv]
2021-04-16 the central hub pcb 1-clickbom file had items from Flypi. this commit removes them and removes duplication from 1-clickbom.csv and 1-clickbom.tsv
    [1-click-bom.csv, 1-click-bom.tsv]
2021-04-16 add a couple of missing components on the 1-click-boms
    [1-click-bom.csv]
2021-04-20 fix 1-click-bom hp led switch
    [1-click-bom.csv]
2021-04-20 add cable assemblies plus housing to 1-click-boms
    [1-click-bom.csv]
2021-05-17 Add driver board
    Driver board is a next iteration of peltier board
    [1-click-bom.csv, driver.kicad_pcb, driver.sch, peltier-B_Adhes.gbr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]
2021-05-17 Add gerbers and change BOM
    [1-click-bom.csv, driver-B_Adhes.gbr, driver-B_CrtYd.gbr, driver-B_Cu.gbr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]
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2021-07-30 fix temp breakout board bug: 5V and gnd were shorted
    [temp_breakout-B_Adhes.gbr, temp_breakout-B_CrtYd.gbr, temp_breakout-B_Cu.gbr, temp_breakout-B_Fab.gbr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]
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2021-10-14 Add ESP32 5V trace and minor changes
    ESP32 is now connected to the same line as Raspberry Pi that should reduce the noise.
    Add new screenshot to the temperature breakout board
    [beehive-B_Adhes.gbr, beehive-B_CrtYd.gbr, beehive-B_Cu.gbr, beehive-B_Fab.gbr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]
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2021-10-25 fix broken file
    [testing_board.sch]
2021-12-02 Update HP switch
    Update wrong tracing and connections on HP switch
    [hp_led_switch-B_Adhes.gbr, hp_led_switch-B_CrtYd.gbr, hp_led_switch-B_Cu.gbr, hp_led_switch-B_Fab.gbr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]
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2022-01-15 modify central hub according to 'review boards issue' and add some media files
    [1-click-bom.csv, beehive-B_Adhes.gbr, beehive-B_CrtYd.gbr, beehive-B_Cu.gbr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]
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2022-01-16 correct folder name
    [temp_breakout-B_Adhes.gbr, temp_breakout-B_CrtYd.gbr, temp_breakout-B_Cu.gbr, temp_breakout-B_Fab.gbr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]
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2022-02-11 Update enclosure
    - Change shape of the ,ain support from circle to triangle for easier 3D printing
    - Increase tolerances
    - Make PCB cover more rigid and add missing middle line with rails
    - Increase height of internal and main supports
    [internal support_v2-Body.stl, internal support_v2.FCStd, internal support_v3-BodyPad001.stl, internal support_v3.FCStd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]
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2022-08-05 Update IR sensor
    MOSFET was wrongly connected to the LED thus rendering the PCB unusable. Now, it is connected the right way
    [ir_sensor-B_Adhesive.gbr, ir_sensor-B_Courtyard.gbr, ir_sensor-B_Cu.gbr, ir_sensor-B_Fab.gbr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]
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2023-03-09 Update IR sensor to v0.4
    IR sensor board updated to version 0.4:
    - removed MOSFET switch;
    First of all, it was supposed to be IRFL44 , L version which can be used with logic levels. But instead we put IRFZ which barely opens at 3.3 V and thus cannot be effectively used here. Moreover, dur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
    - Add additional phototransistor connector
    - Add additional IR LED connector
    [ir_sensor-B_Adhesive.gbr, ir_sensor-B_Courtyard.gbr, ir_sensor-B_Cu.gbl, ir_sensor-B_Fab.gbr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]
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2023-03-10 Add v0.2 version of the training board
    New v0.2 version of the training board:
    - added rotary encoder
    - removed one of relays
    - fixed wiring on potentiometers
    - removed h-bridge LEDs
    - added module to demonstrate how jumper wires work
    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
    [Bourns_Inc._-_PEC16-4015F-N0024.step, training_board_v02-B_Cu.gbl, training_board_v02-B_Mask.gbs, training_board_v02-B_Paste.gbp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]
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2025-05-20 Fix grove_adaptor_panel edge cuts (using KiCad 9)
    [grove_adaptor_panel-B_Adhesive.gbr, grove_adaptor_panel-B_Cu.gbr, grove_adaptor_panel-B_Fab.gbr, grove_adaptor_panel-B_Mask.gbr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]
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

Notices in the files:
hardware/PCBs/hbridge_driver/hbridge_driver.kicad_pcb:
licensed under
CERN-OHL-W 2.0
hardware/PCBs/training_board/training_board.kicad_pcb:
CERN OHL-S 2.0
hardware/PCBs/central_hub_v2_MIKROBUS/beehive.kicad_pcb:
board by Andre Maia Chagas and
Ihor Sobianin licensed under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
